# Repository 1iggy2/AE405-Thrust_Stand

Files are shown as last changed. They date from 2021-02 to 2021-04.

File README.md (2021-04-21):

# AE405 Thrust Stand

Aero 405 Thrust Stand Project

*By Cameron Gable (1iggy2), Anthony Russo, Hogan Hsu, Sergio Ramirez Sabogal, Brian Sandor*

This project is aimed towards providing a thrust testing stand for brushless electric motors
and propellers used by student project teams as part of Professor George Halow’s AERO 495
course. Prof. Halow has indicated that there is currently a need for some of the project teams that
are part of his course to have an easy way to test the thrust capabilities of their electric motors and
propellers for applications ranging from quadcopters to fixed wing aircraft. Our project concept is
therefore a proposal to design, build, and test a modular thrust test stand that allows for multiple
motor and propeller sizes to be tested safely and effectively by any of the teams participating in
AERO 495. This test stand will use sensors to measure thrust, torque, voltage, current, and RPM
and involve a processing system for automated data collection for simple export to software like
Excel or MatLab for analysis.

<p align="center">
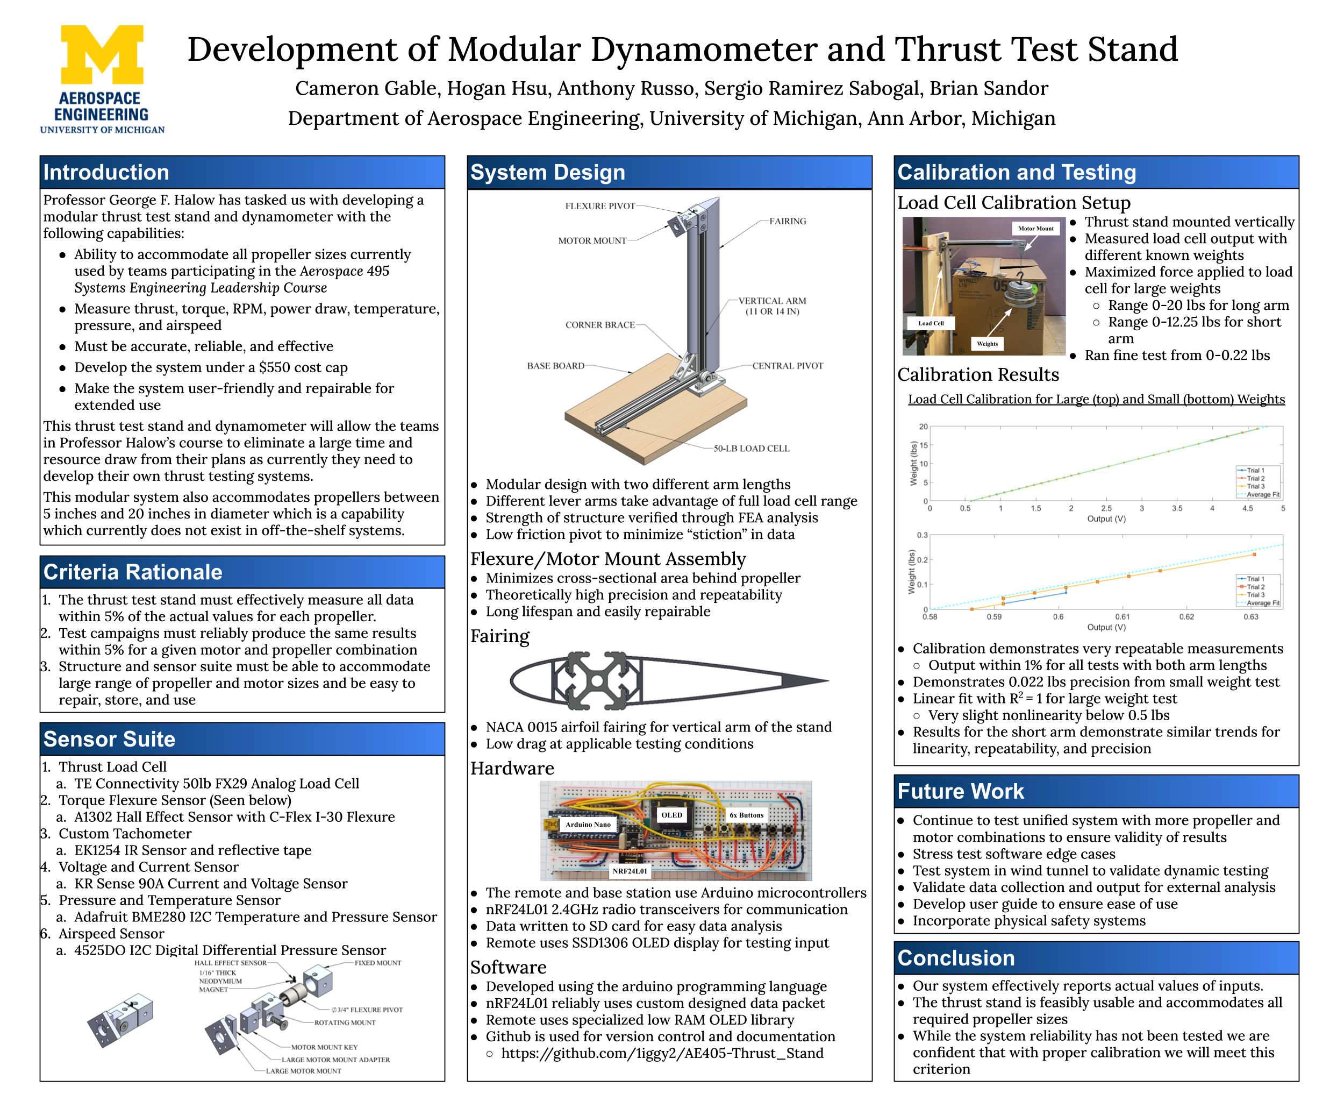
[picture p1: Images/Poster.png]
  
</p>

Table of Contents
=================

<!--ts-->
   * [Instruction Manual](#instruction-manual)
      * [Safety Considerations](#safety-considerations)
      * [How to Use the Remote](#how-to-use-the-remote)
      * [How to Use the Base Station](#how-to-use-the-base-station)
   * [Construction Guide](#construction-guide)
      * [Wiring](#wiring)
        * [Remote](#remote)
        * [Base Station](#base-station)
      * [Thrust Stand](#thrust-stand)
   * [Design Justification](#design-justification)
      * [Code](#code)
        * [Base Station Logic](base-station-logic)
        * [Remote GUI Explaination](remote-gui-explaination)
      * [Physical Structure Analysis and Testing](physical-structure-analysis-and-testing)
        * [Thrust Stand Simulation](thrust-stand-simulation)
<!--te-->

## Instruction Manual

### Safety Considerations

Be careful when near spinning and/or powered propellers they can and will maim you. Please remove all propellers while working on the thrust stand. Propellers of all sizes are dangerous and deserve your respect. Please use the remote to remain clear of the spinning blades of death, and ensure you have a way to break the physical circuit from a distance.

(http://www.youtube.com/watch?v=q4shbLB9U7Q "")

### How to Use the Remote

The remote connects to the base station using an nRF24L01 radio transciever. When powering on the remote from a computer or USB power supply you will be prompted to select a test to perform. The test selection buttons are on the left hand side of the remote and ordered as seen below:
* TS - Throttle Sweep
* CT - Constant Throttle
* ST - Stress Test
<p align="center">
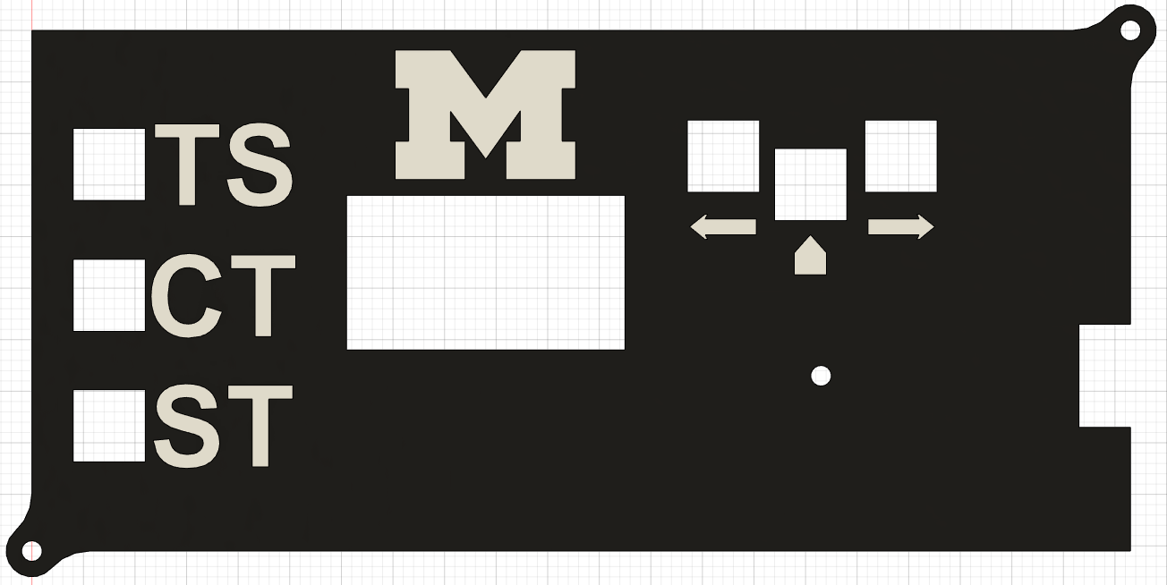
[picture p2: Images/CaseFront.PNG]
  
</p>
<p align="center">
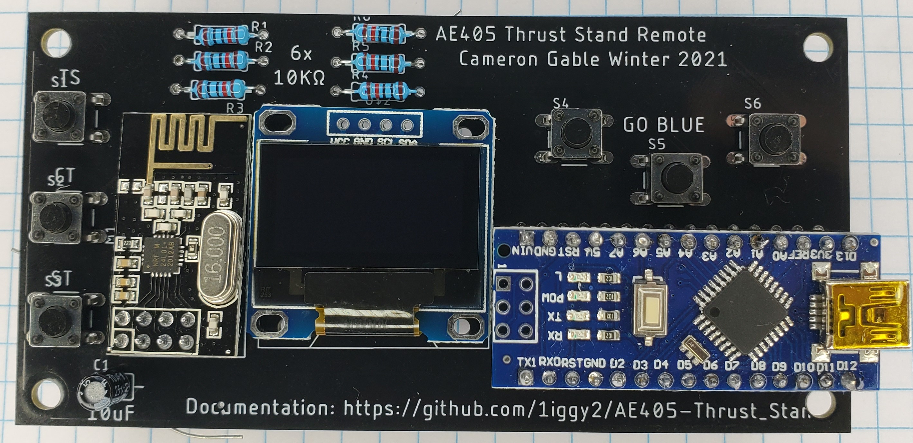
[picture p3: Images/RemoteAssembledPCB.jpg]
  
</p>
You then will use the ← (left), → (right), and ⌂ (select) buttons to enter your chosen testing parameters. These parameters are:
  
| Parameter |     Description    |  Throttle Sweep |    Constant Throttle    |     Stress Test     |
|:---------:|:------------------:|:---------------:|:-----------------------:|:-------------------:|
|     A     |      Test Type     |        1        |            2            |          3          |
|    BBB    |  Primary Throttle  | Bottom of Sweep | Constant Throttle Value | High Throttle Value |
|    CCC    | Secondary Throttle |   Top of Sweep  |           N/A           |  Low Throttle Value |
|    DDD    |      Test Time     | Total Test Time |     Total Test Time     |   Total Test Time   |
|    EEE    |      Step Time     |    Step Time    |           N/A           |    Switching Time   |

Before clicking to confirm your test selection and start your test you will be presented these values as a final check before sending the data to the base station. This will appear in the form:

* A:BBB:CCC:DDD:EEE

After the data is sent to the base station and the test begins simply click the ⌂ (select) button to send a cancel signal to the base station. In case of communication failure it is always important to have a safe method to physically break the circuit in the case of a catastrophic testing failure. 

### How to Use the Base Station

The base station is a rather hands off piece of equipment. You should not be interacting with it during testing, only monitoring. You may want to set your own safety parameters or recalibrate the test stand. In that case I recommend modifying the parameters in the base station file: [Mega_BaseStation.ino](https://github.com/1iggy2/AE405-Thrust_Stand/blob/main/Mega_BaseStation/Mega_BaseStation.ino) If you do this please submit your calibration to this Github page for posterity. To gather data you will need to insert a FAT32 or FAT16 formatted microSD card into the [Adafruit MicroSD card breakout board+](https://www.adafruit.com/product/254) for the data to be recorded. The data will be recorded to the microSD card in the format shown below. 

| AERO 405 Thrust Stand |                       Winter 2021                      |         |             | Cameron Gable |
|:---------------------:|:------------------------------------------------------:|:-------:|:-----------:|:-------------:|
| Find Documentation at:| [Github](https://github.com/1iggy2/AE405-Thrust_Stand) |         |             |               |
|                       |                                                        |         |             |               |
|  Ambient Conditions:  |                                                        |         |             |               |
|      Temperature:     |                          VALUE                         | Celsius |             |               |
|       Pressure:       |                          VALUE                         | Pascals |             |               |
|                       |                                                        |         |             |               |
|       Thrust(N)       |                          Volts                         |   Amps  | Torque(n-m) |      RPM      |
|         VALUE         |                          VALUE                         |  VALUE  |    VALUE    |     VALUE     |

At this time analysis software is not being developed. It is an important feature to this project, and the relevant issue can be found [here.](https://github.com/1iggy2/AE405-Thrust_Stand/issues/9)

## Construction Guide

### Wiring

#### Remote
The wiring diagram for the remote has been completed in EAGLE. Completed PCB design Gerber files can be found [here.](https://github.com/1iggy2/AE405-Thrust_Stand/tree/main/CAD/RemotePCB) The connections on the diagram below are accurate for anyone who prefers to manufacture it on perf board. (Assembling via a PCB is certainly easier though).

<p align="center">
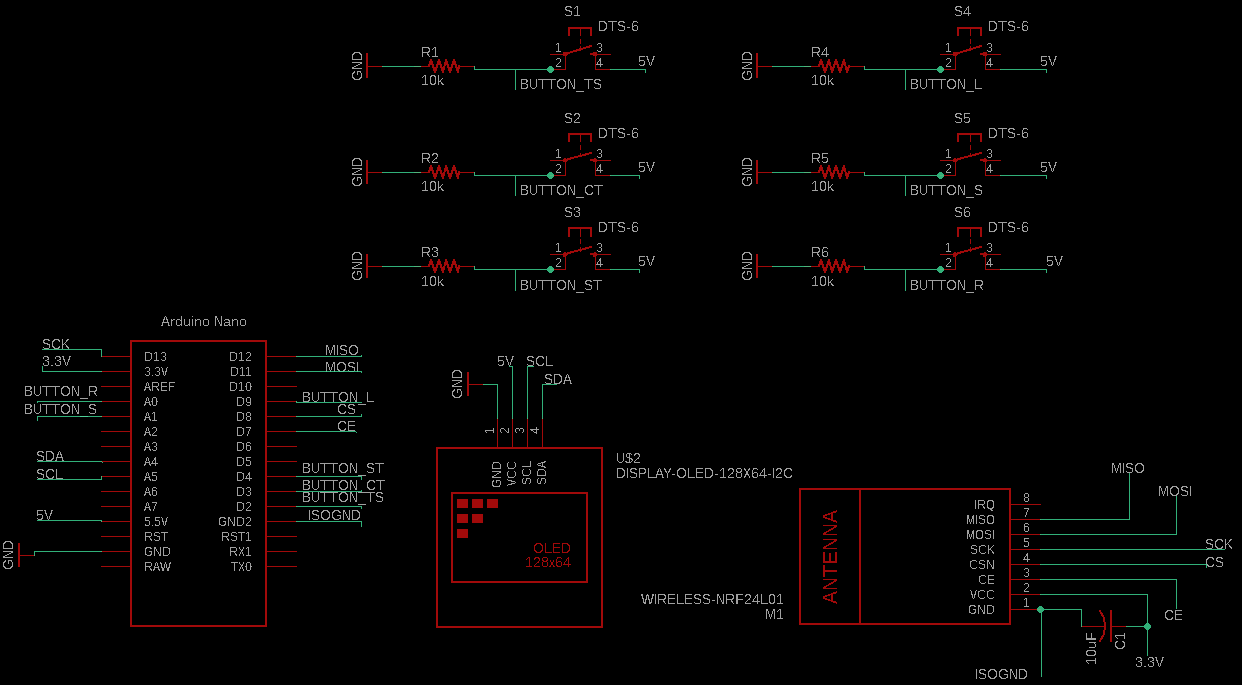
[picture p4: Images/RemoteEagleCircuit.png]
  
</p>

#### Base Station
The wiring diagram for the base station was also completed in EAGLE. However, a PCB has not yet been designed and remains an [issue](https://github.com/1iggy2/AE405-Thrust_Stand/issues/3) for future work.

<p align="center">
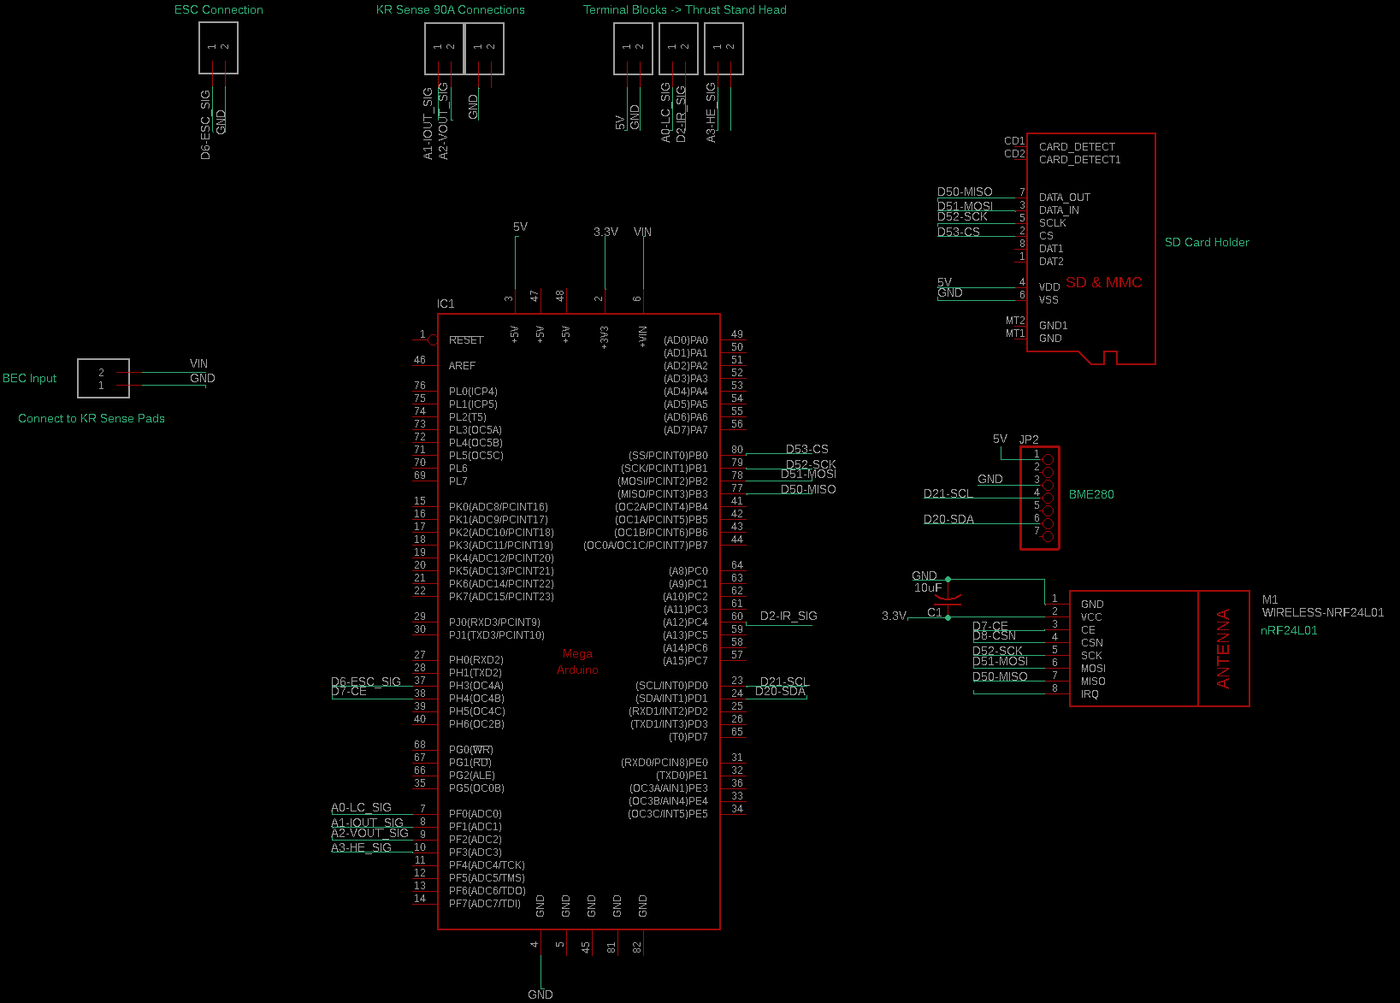
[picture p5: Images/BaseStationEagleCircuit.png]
  
</p>
Please note in the EAGLE image above the pin locations are not accurate on the Arduino Mega, instead the nets have been named [PIN-PURPOSE].

### Thrust Stand

Our thrust stand has been designed with modularity as the main objective. The interchangeable
vertical arm lengths allow for testing to occur for a variety of propeller and motor sizes. This also
allows for the thrust stand to operate in both large and small wind tunnels, making test scheduling more convenient for the users. Our motor mounting plates will allow for the mounting of
various motors with different bolt patterns. The various sizes of these plates will allow for testing
on small motors and large motors on the same stand. 

Long Arm Render             |  Short Arm Render
  :-------------------------:|:-------------------------:
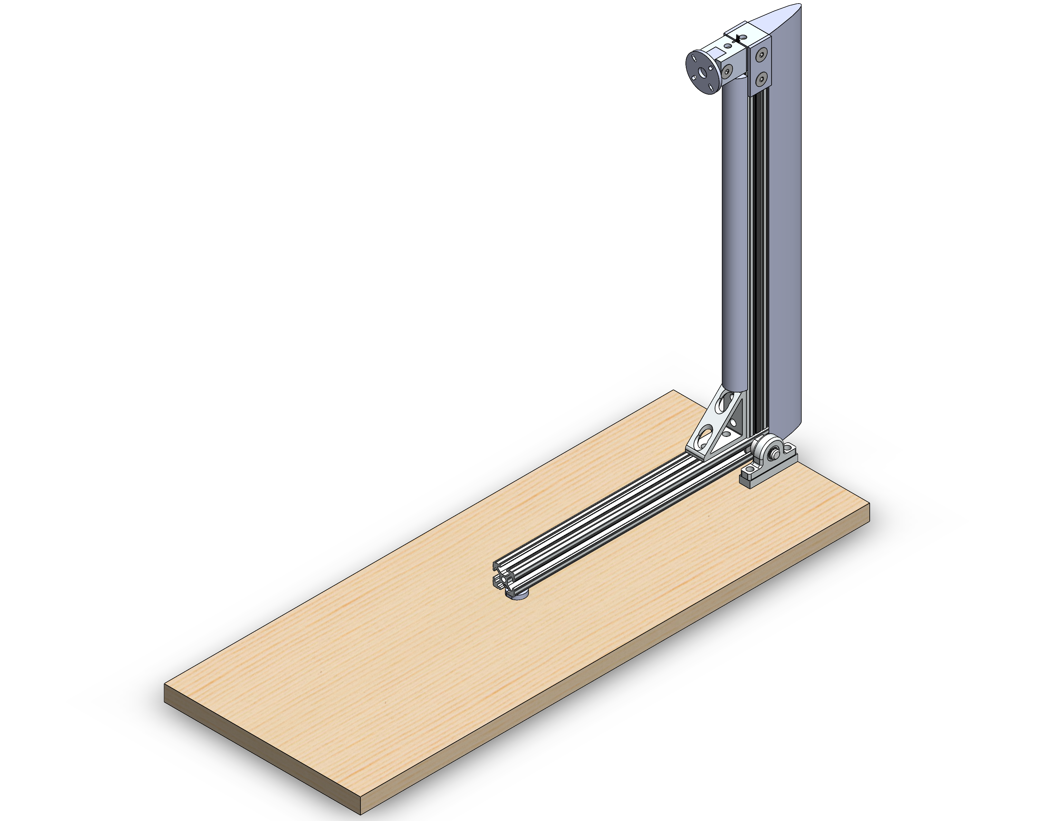
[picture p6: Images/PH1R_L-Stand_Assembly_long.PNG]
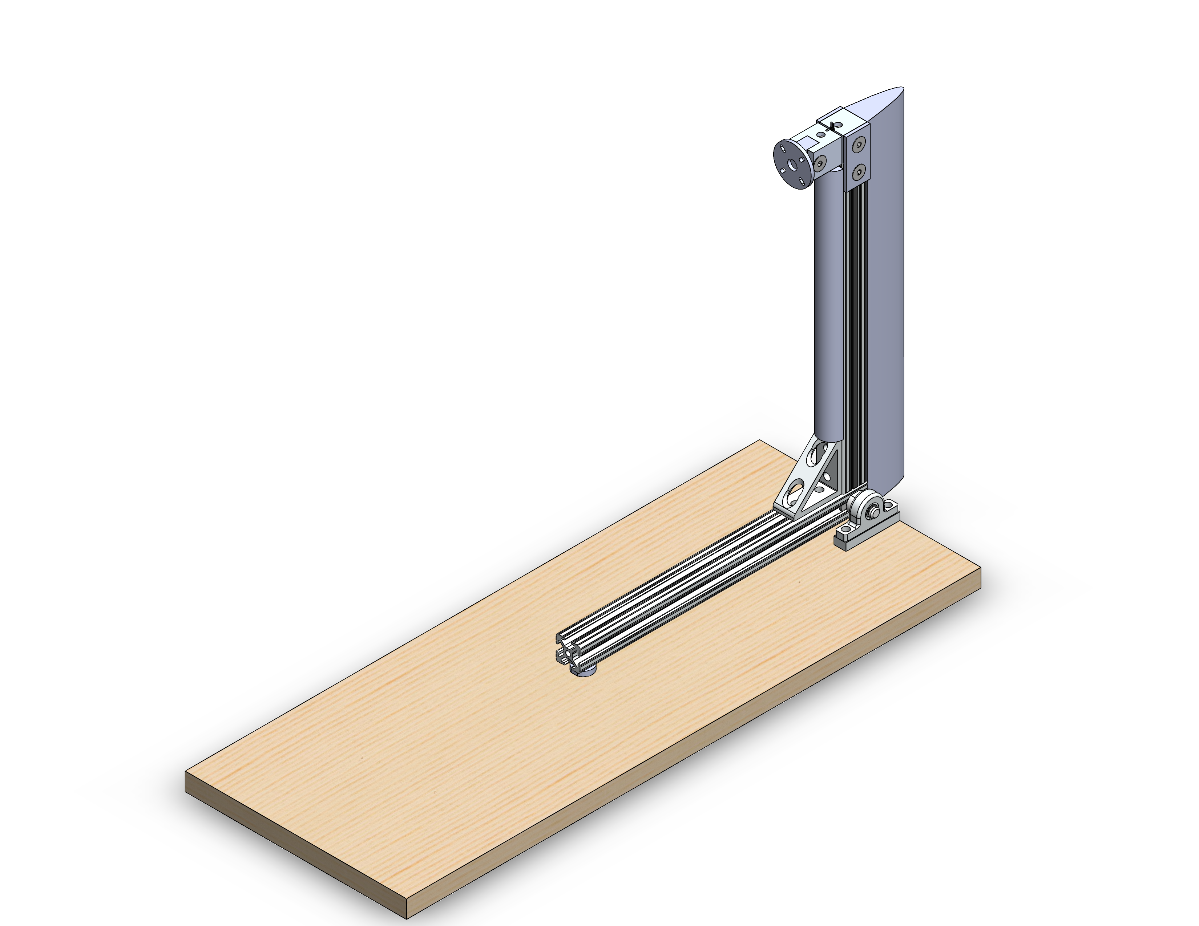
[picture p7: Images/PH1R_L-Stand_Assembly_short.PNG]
  |  

Our unique flexure torque measurement
device, seen below, allows for torque data to be collected from all ranges of motor sizes that fit on the thrust
testing stand. This innovation increases the effectiveness and accuracy of the data from other more
traditional torque measurement solutions. These system design choices increase the effectiveness
of our thrust stand and allow it to meet a wide variety of team’s thrust testing needs.
<p align="center">
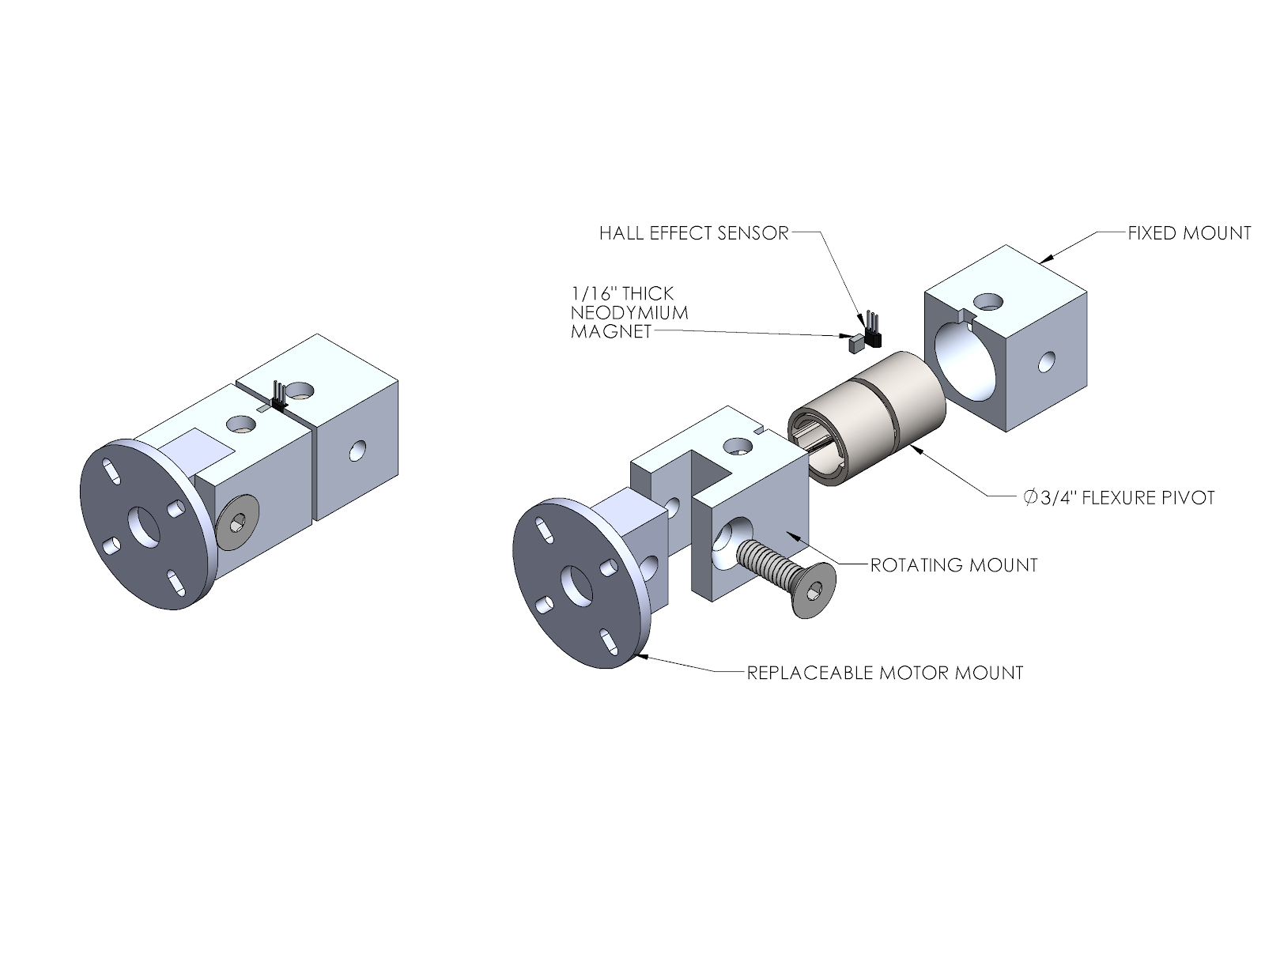
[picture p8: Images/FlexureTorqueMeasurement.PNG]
  
</p>
Our design also features a pivot comprised of two pillow blocks to minimize any stiction, or static friction. A beautiful render of this pivot is shown below. A majority of the parts purchased for the structural construction came from McMaster Carr.

<p align="center">
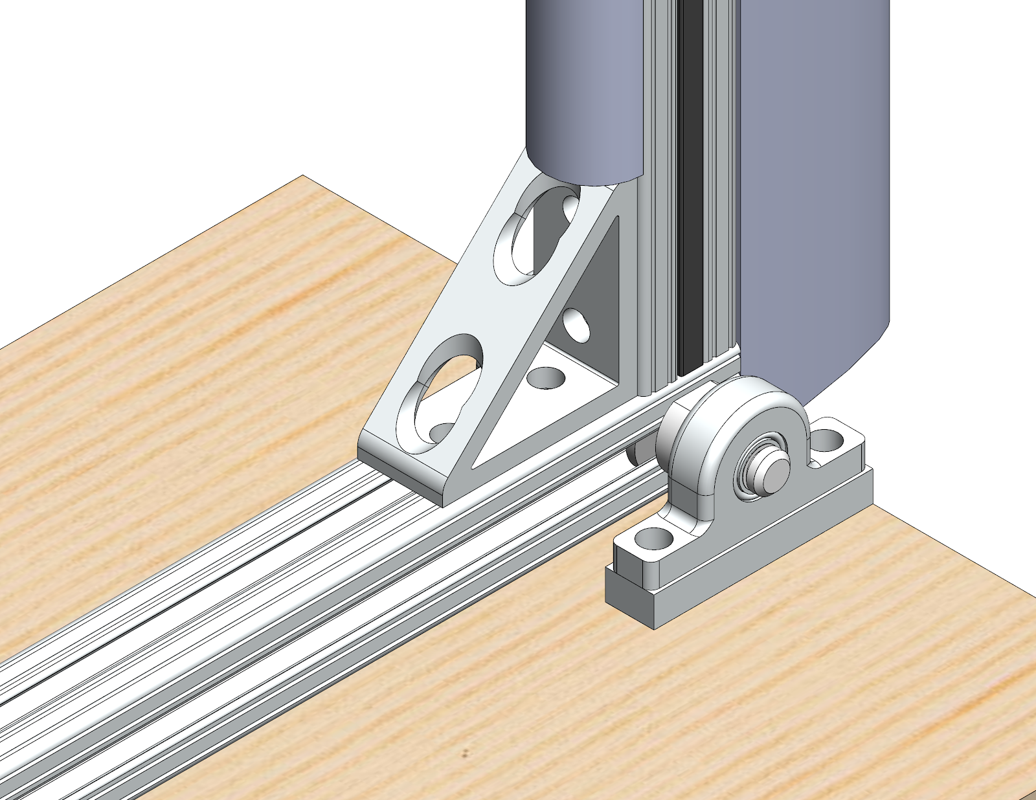
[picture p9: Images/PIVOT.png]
  
</p>

## Design Justification

### Code

#### Base Station Logic

The Base Station is the measurement and data acquistion hub of this project. Tests will be run based on the Menu ID sent from the remote. Raw sensor output, calibration, and settings will be accessed via a physical button press and the serial monitor. This is due to RAM limitations in the Arduino Nano powering the Remote. A full flowchart of the logic is provided below.

<p align="center">
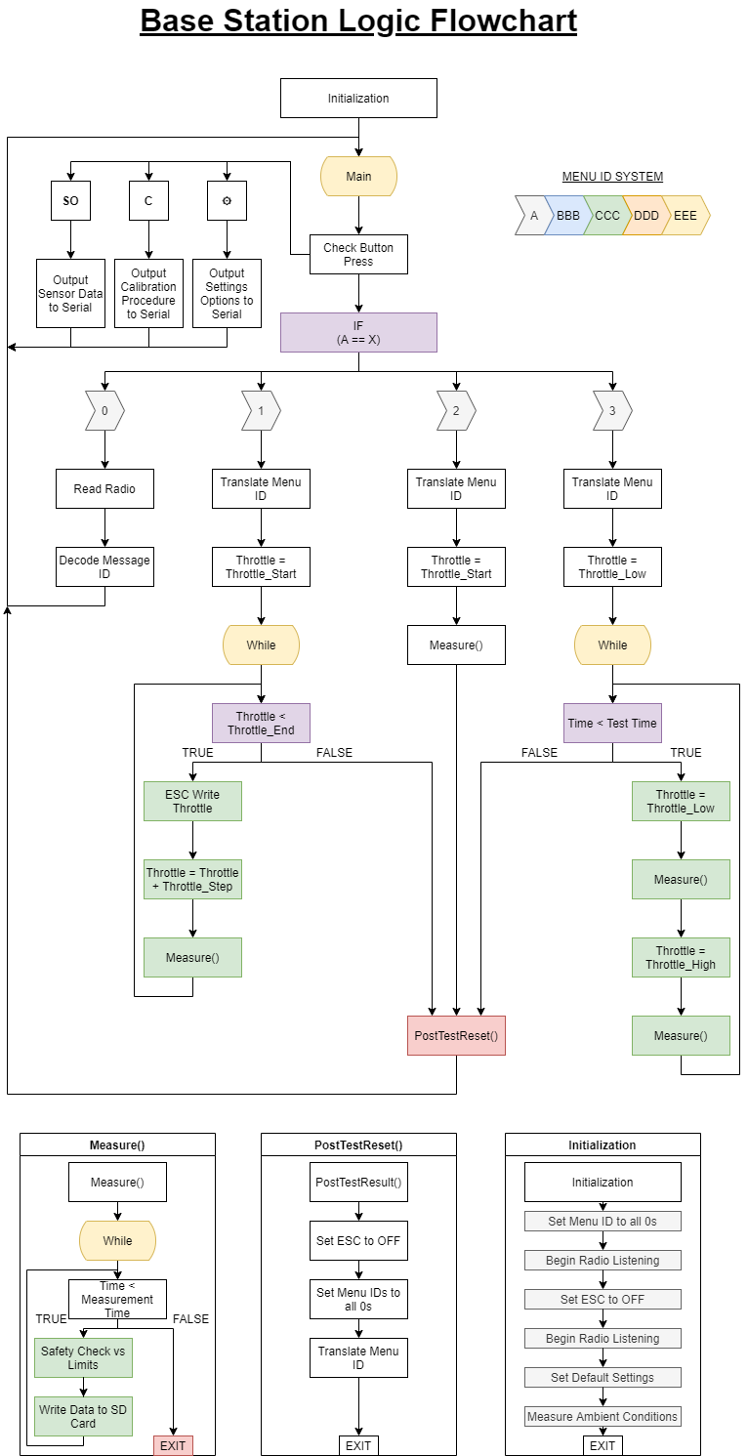
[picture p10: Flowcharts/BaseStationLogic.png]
  
</p>

#### Remote GUI Explaination

After initial testing of the remote GUI intiailly proposed it was apparent that the Arduino Nano did not have enough RAM to display the fully fleshed out GUI. In order to combat this we have designed a low menu count GUI to optimize the remote. This menu uses a minimal amount of unique screens to lower the RAM usage. The image below is the design flowchart for the optimized remote.

<p align="center">
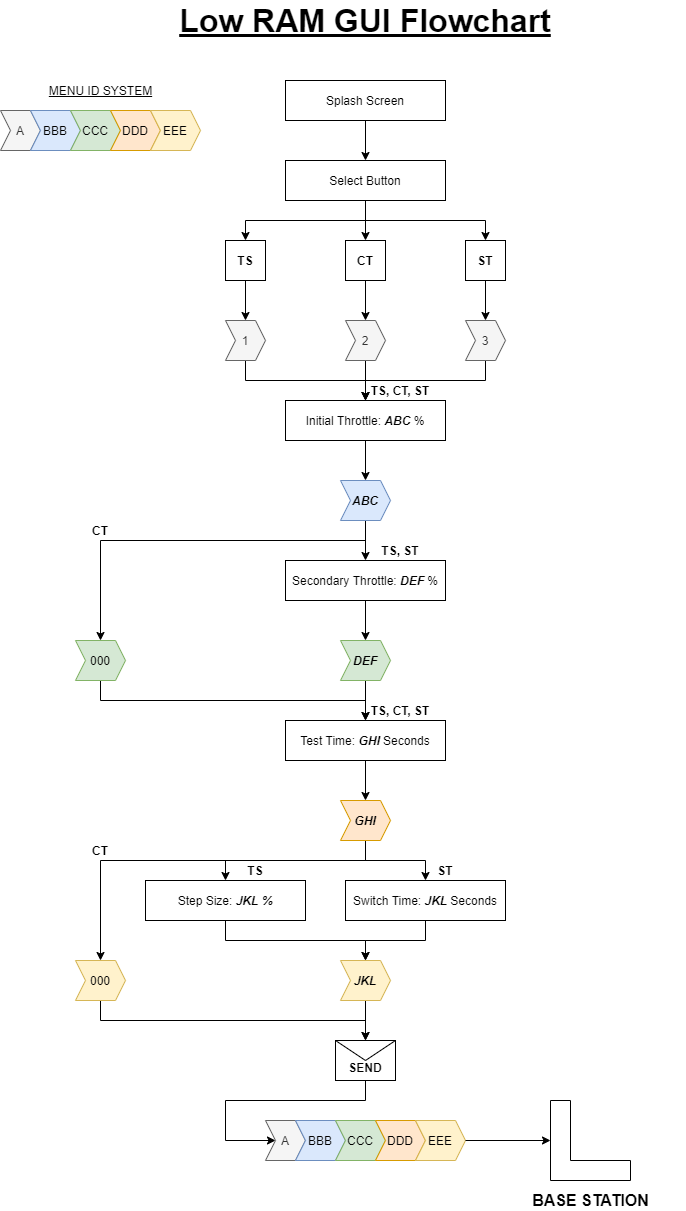
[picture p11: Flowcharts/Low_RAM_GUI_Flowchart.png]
  
</p>

### Physical Structure Analysis

#### Thrust Stand Simulation

In order to model the thrust stand system in FEA many of the complex structures
were simplified. This included the flexure assembly being modelled as a rectangular block and
the bearing pivot being modelled as a bearing fixture. The CAD model was done in Solidworks
and the FEA was done in the Solidworks built-in simulation tool. The load cell and the sides of the
pivot were modelled as roller/slider fixtures so that they would be constrained in the plane but
can move laterally. The built-in 6061 aluminum alloy material model was applied to the model
due to convenience, which has the same properties as the 6105-T5 alloy, just a lower yield strength.
The mesh was generated using Solidworks’ automated mesh tool, but mesh control was applied
in order to ensure that there were at least 3 elements across each dimension to accurately model
the problem. In the image below, a zoomed in display of the maximum stress point is shown along with
the mesh for the max loading condition of 20 lbf of thrust and 15 lbf-in of torque on the long
arm model. The maximum stress ended up being in the same region for all the simulations, right
where the 90◦ bracket met the horizontal arm.

<p align="center">
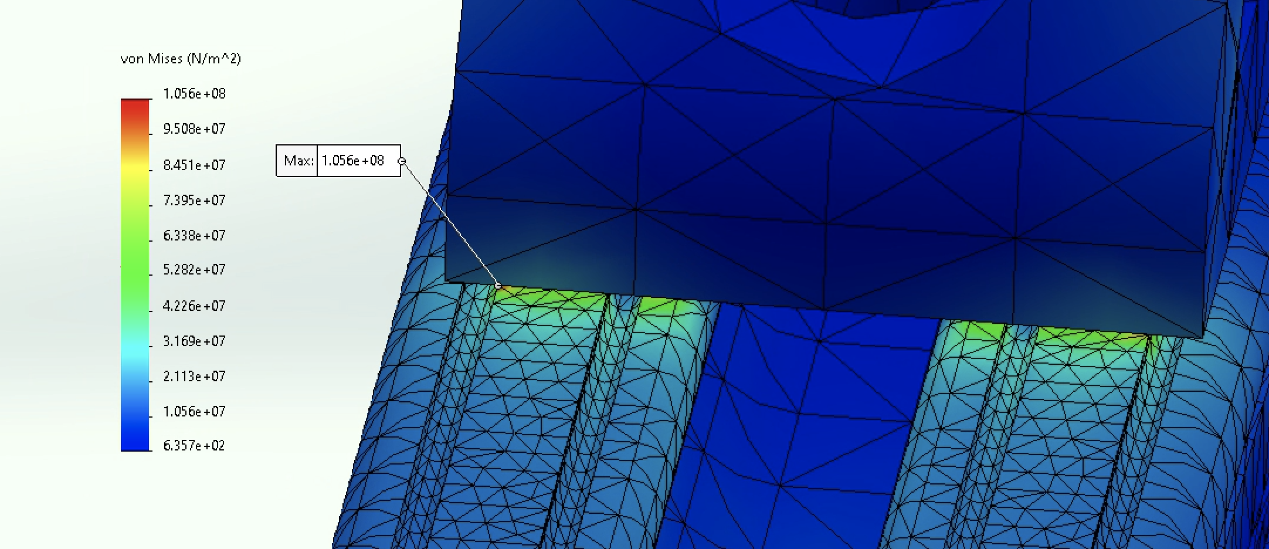
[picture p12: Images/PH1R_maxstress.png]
  
</p>

Another accuracy concern is the drag produced by inlet air during wind tunnel testing, particularly
on the vertical arm of the test stand. The load cell measuring thrust will not be able to distinguish between this drag force and a thrust difference, thus reducing accuracy. To make sure that
our measurement is as accurate as possible during these testing circumstances, we surveyed various cross-sectional shapes of the vertical beam using CFD simulations. STAR-CCM+ CFD simulations were used to model the drag of the
stand. Because the only variable between these design is the vertical beam cross-section, simulations were performed using the 15 inch beam by itself, with semicircular fairings, and with one
semicircular fairing on the front face and an elliptical section on the rear face to give the overall cross-section an airfoil shape. Seen in the table below.

| No Fairing | Semi-Circular Fairing | Airfoil Fairing |
|------------|-----------------------|-----------------|
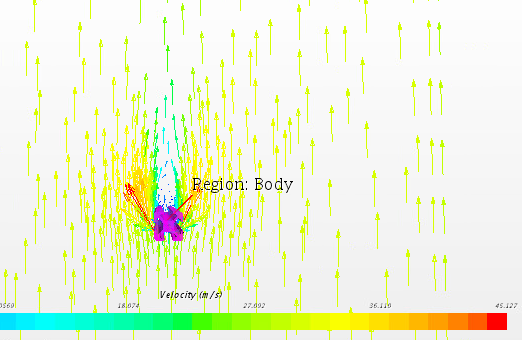
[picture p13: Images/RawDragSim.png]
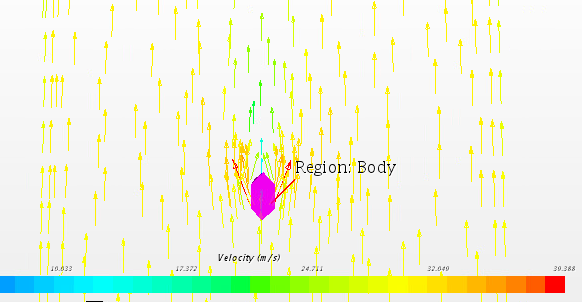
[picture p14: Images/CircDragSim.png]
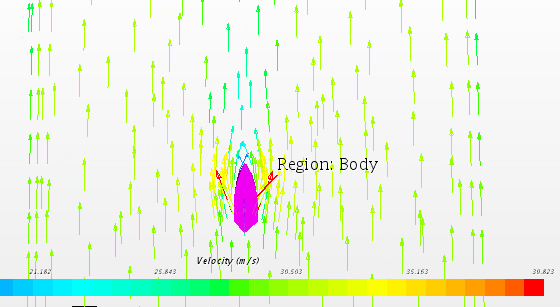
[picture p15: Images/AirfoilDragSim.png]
|       |                  |            |

The simulations were then run with the respective beam suspended,
centered in a simulated 2 foot X 2 foot wind tunnel using iterations with intake airspeed of 11, 22,
34, 45, 56, and 67 miles per hour. The results are shown in the table below.

<p align="center">
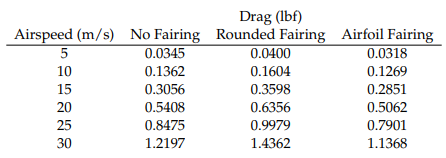
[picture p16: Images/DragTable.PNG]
  
</p>

Plotted into a graph:

<p align="center">
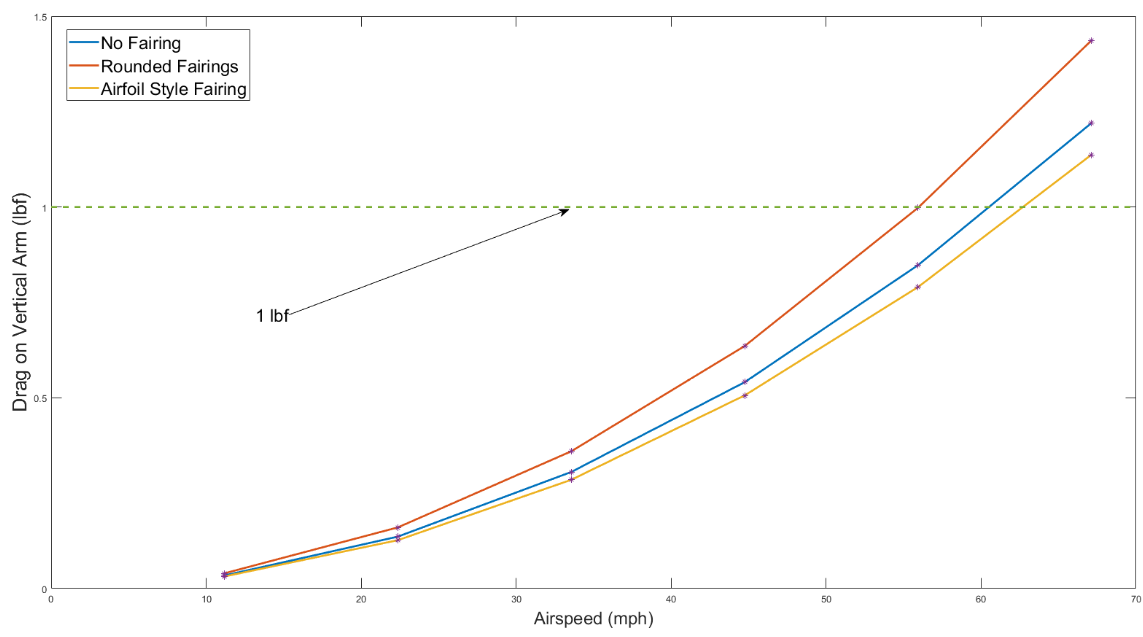
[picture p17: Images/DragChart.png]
  
</p>

With this information we are designing a 3D printed airfoil to slot into the 8020 aluminium extrusion. We will also be putting our structure, shrouded with an aerodynamic
fairing, into the wind tunnel and testing the amount of drag that the system generates with the
goal of minimizing this effect. This will be to validate our simulations. 

We chose to use a NACA 0015 airfoil fairing for the vertical arm of the stand.

<p align="center">
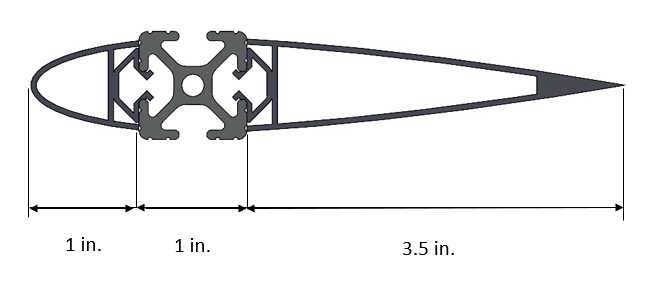
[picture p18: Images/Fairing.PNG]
  
</p>

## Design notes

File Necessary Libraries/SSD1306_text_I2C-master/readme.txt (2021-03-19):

SSD1306_text -- methods
April 2015

init() - call once in setup
clear() - clears screen, sets cursor to 0,0
setCursor(row, pixel_col) - sets cursor to row (0..7) and pixel_column (0..127)
setCursor(row) - sets cursor to row (0..7) and pixel_column=0 
getRow() - returns current row
getCol() - returns current column
setTextSize(size, spacing) - sets text size (1..8) and pixel spacing between chars (0,1,2,...)
setTextSize(size) - sets text size (1..8) and sets spacing to the same value
write(c) - write a single character to the current cursor location with current size/spacing
write(*str) - write a string of characters
write(*buffer, nBytes) - write nBytes of characters from a buffer
sendData(b) - write an 8-bit vertical slice of pixels to the current cursor location

Configuration switches in the .h file provide for choosing hardware SPI, software SPI or I2C
support. Also support for scaled fonts larger than the default 5x7 (size=1) can be enabled/disabled. In addition, improved fonts for the numeric characters 0-9 for sizes 2x, 3x and 8x the 5x7 font size can be enabled/disabled.

With a minimum configuration (H/W SPI and no scaled or larger fonts) a simple "hello world" sketch is about 2500 bytes in size and uses about 50 bytes of RAM. Adding scaled fonts increases the code size somewhat. Adding dedicated larger numeric fonts has a more pronounced effect on code size.

I2C support uses the Wire library which, in addition to adding ~1K of code, adds about 200 bytes of RAM usage, mostly from the five 32-byte buffers in the library.

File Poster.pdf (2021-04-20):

System Design

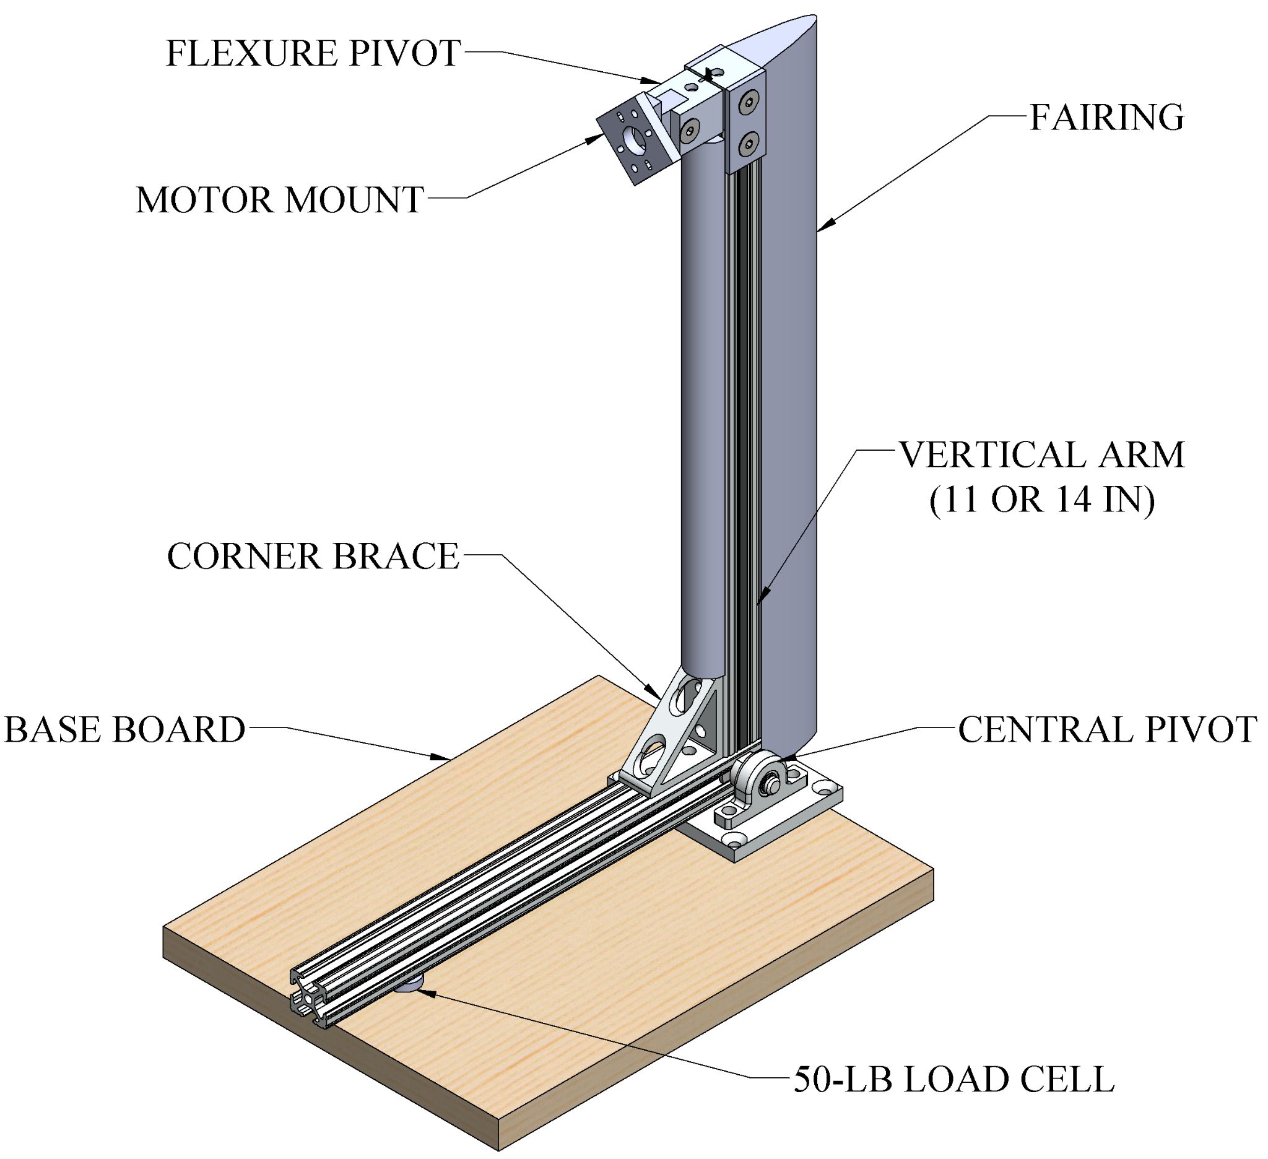
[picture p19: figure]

- Modular design with two different arm lengths
- Different lever arms take advantage of full load cell range
- Strength of structure verified through FEA analysis
- Low friction pivot to minimize “stiction” in data

## Flexure/Motor Mount Assembly

- Minimizes cross-sectional area behind propeller
- Theoretically high precision and repeatability
- Long lifespan and easily repairable

## Fairing

- NACA 0015 airfoil fairing for vertical arm of the stand
- Low drag at applicable testing conditions

## Hardware

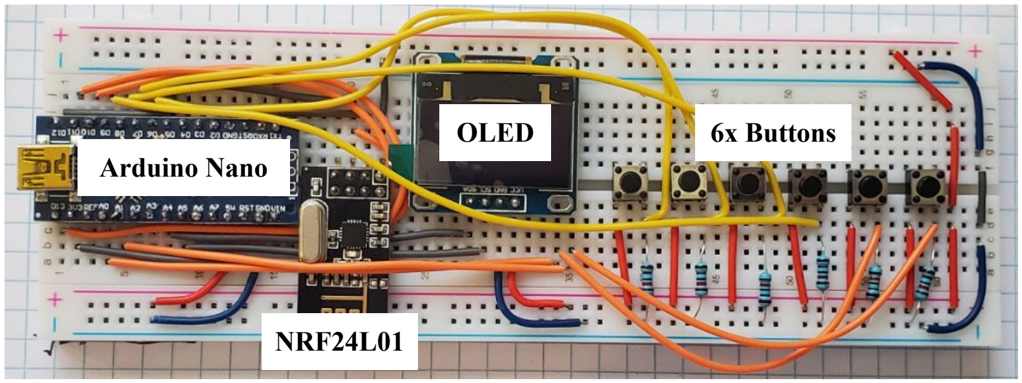
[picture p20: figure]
Arduino Nano; OLED; NRF24L01; 6x Buttons

- The remote and base station use Arduino microcontrollers
- nRF24L01 2.4GHz radio transceivers for communication
- Data written to SD card for easy data analysis
- Remote uses SSD1306 OLED display for testing input

## Software

- Developed using the arduino programming language
- nRF24L01 reliably uses custom designed data packet
- Remote uses specialized low RAM OLED library
- Github is used for version control and documentation
- https://github.com/1iggy2/AE405-Thrust_Stand

# Development of Modular Dynamometer and Thrust Test Stand

## Cameron Gable, Hogan Hsu, Anthony Russo, Sergio Ramirez Sabogal, Brian Sandor Department of Aerospace Engineering, University of Michigan, Ann Arbor, Michigan

Introduction
Professor George F. Halow has tasked us with developing a modular thrust test stand and dynamometer with the following capabilities:
- Ability to accommodate all propeller sizes currently used by teams participating in the Aerospace 495 Systems Engineering Leadership Course
- Measure thrust, torque, RPM, power draw, temperature, pressure, and airspeed
- Must be accurate, reliable, and effective
- Develop the system under a $550 cost cap
- Make the system user-friendly and repairable for extended use
This thrust test stand and dynamometer will allow the teams in Professor Halow’s course to eliminate a large time and resource draw from their plans as currently they need to develop their own thrust testing systems.
This modular system also accommodates propellers between 5 inches and 20 inches in diameter which is a capability which currently does not exist in off-the-shelf systems.

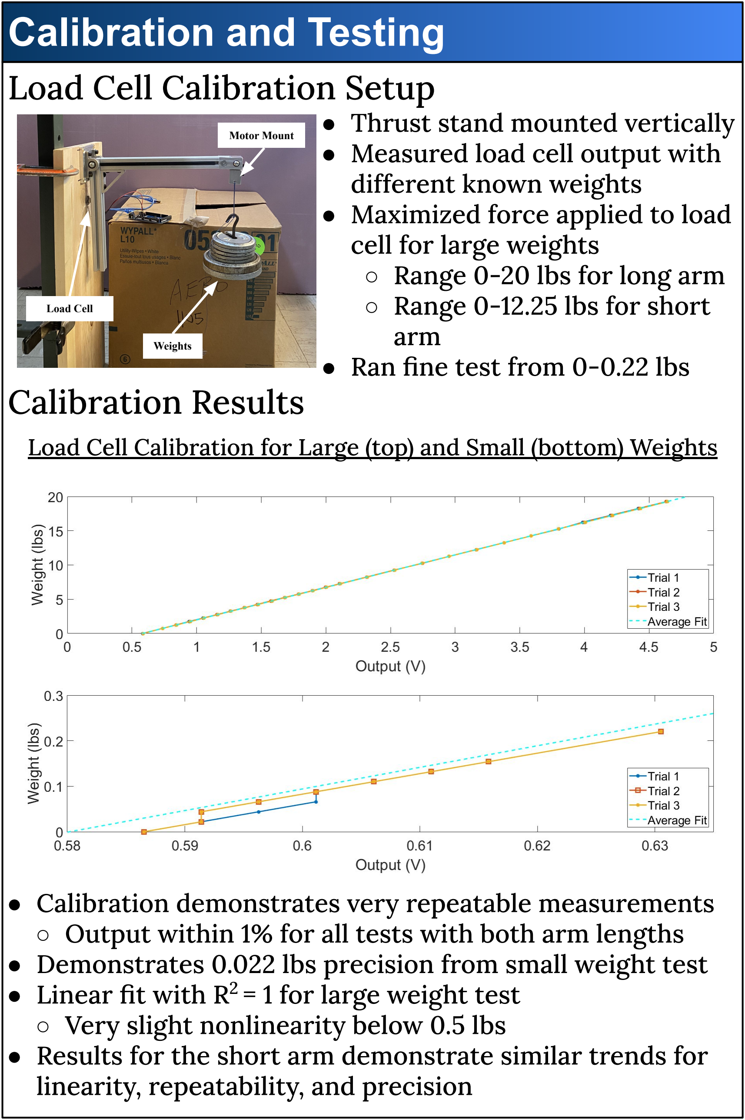
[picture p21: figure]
Calibration and Testing Load Cell Calibration Setup ● Thrust stand mounted vertically ● Measured load cell output with different known weights ● Maximized force applied to load cell for large weights ○ Range 0-20 lbs for long arm ○ Range 0-12.25 lbs for short arm ● Ran fine test from 0-0.22 lbs; Calibration Results; ● Linear fit with R; 2 = 1 for large weight test; linearity, repeatability, and precision; Weights; Load Cell; Motor Mount

Load Cell Calibration for Large (top) and Small (bottom) Weights

- Calibration demonstrates very repeatable measurements
- Output within 1% for all tests with both arm lengths
- Demonstrates 0.022 lbs precision from small weight test
- Very slight nonlinearity below 0.5 lbs
- Results for the short arm demonstrate similar trends for

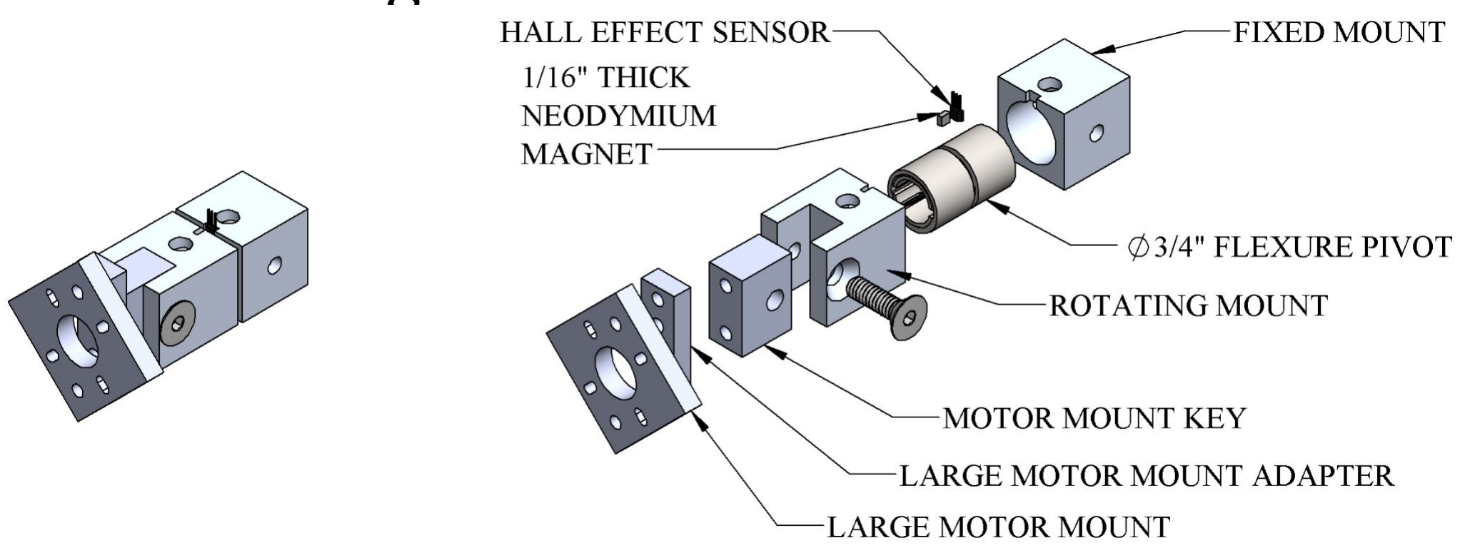
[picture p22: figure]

Conclusion
- Our system effectively reports actual values of inputs.
- The thrust stand is feasibly usable and accommodates all required propeller sizes
- While the system reliability has not been tested we are confident that with proper calibration we will meet this criterion

Criteria Rationale
1. The thrust test stand must effectively measure all data within 5% of the actual values for each propeller.
2. Test campaigns must reliably produce the same results within 5% for a given motor and propeller combination
3. Structure and sensor suite must be able to accommodate large range of propeller and motor sizes and be easy to repair, store, and use

Sensor Suite
1. Thrust Load Cell
a. TE Connectivity 50lb FX29 Analog Load Cell
2. Torque Flexure Sensor (Seen below)
a. A1302 Hall Effect Sensor with C-Flex I-30 Flexure
3. Custom Tachometer
a. EK1254 IR Sensor and reflective tape
4. Voltage and Current Sensor
a. KR Sense 90A Current and Voltage Sensor
5. Pressure and Temperature Sensor
a. Adafruit BME280 I2C Temperature and Pressure Sensor
6. Airspeed Sensor
a. 4525DO I2C Digital Differential Pressure Sensor

Future Work
- Continue to test unified system with more propeller and motor combinations to ensure validity of results
- Stress test software edge cases
- Test system in wind tunnel to validate dynamic testing
- Validate data collection and output for external analysis
- Develop user guide to ensure ease of use
- Incorporate physical safety systems

# References

“NACA 0015,” Airfoil Tools. 2021 http://airfoiltools.com/airfoil/details?airfoil=naca0015-il

## “Brushless Motor and Propeller Thrust Stands,” RCbenchmark Available:https://www.rcbenchmark.com/

## Hossain M. R., Krouglicof, N.,"Propeller Dynamometer for Small Unmanned Aerial Vehicle,"CCECE2010, 2010.https://ieeexplore.ieee.org/document/5575152

## Asson, K. M., Dunn, P. F., "Compact Dynamometer System that Can Accurately Determine

PropellerPerformance,"Journal of Aircraft, vol. 29, pp. 8-9,

## 1992.https://arc-aiaa-org.proxy.lib.umich.edu/doi/abs/10.2514/3.46118

## Li, H. H., Davis, K. R., Davy, M. H. Green, S. I. "A Marine Propeller Aerodynamic Test

Facility,"Strain, vol. 43, pp. 125-131,

## 2007.https://doi-org.proxy.lib.umich.edu/10.1111/j.1475-1305.2007.00325.x

## "AA Standards Grade 6105 T5." Matmatch Available:https://matmatch.com/materials/alky16105229t50-aa-standards-grade-6105-t517

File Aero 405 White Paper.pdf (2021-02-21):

## White Paper: Modular Thrust Stand

Anthony Russo, Brian Sandor, Cameron Gable, Hogan Hsu, Sergio Ramirez Sabogal
February 3rd
, 2021

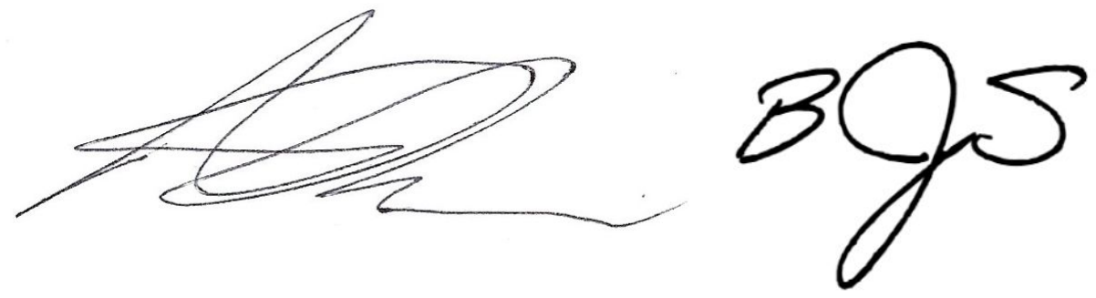
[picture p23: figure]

Description
This project identifies a direct need from the Aerospace 495 System Engineering Leadership Course (Aero 495) for testing hardware specifically for electric propeller-driven aircraft. The course focuses on leveraging three existing Student Project Teams: Michigan Vertical Flight Technology (MVFT), Michigan Drone Racing (MDR), and MACH (University of Michigan AIAA Design, Build, Fly Team). These three teams all rely on electric motors and propellers to propel their vehicles for competition. Each team uses different motor and propeller combinations ranging from roughly 5 inch propellers (MDR) to propellers larger than 15 inches (MVFT) and all teams need to perform in-house thrust testing to ensure consistent and reliable performance of their motors. As such, this team has been formed to develop a thrust testing system that can adequately meet the needs of the teams in Aero 495 as well as any future teams that may participate in the course or any other student project teams that use electric motors and propellers as their main propulsion system.
Our thrust testing system must be able to accommodate a range of propeller sizes and record thrust, revolutions per minute (RPM), motor torque, and power draw, as well as any other data that the aforementioned teams may want to analyze during their testing. Our system will also be safe, reliable, easy to repair and operate, meet the course cost cap, and use any and all available resources. We will be developing this testing system to be utilized by the aforementioned course and project groups. The goal being to create and test a more quality product than what is available off-the-shelf with much more operational flexibility and much higher quality results. This will be developed over the course of the Winter 2021 semester at the University of Michigan Aerospace Engineering facilities with the oversight and support of Professors George Halow (Aero 495) and Tim Smith (Aero 405).

Justification
The creation of the Aero 495 System Engineering Leadership Course this year has brought together many aerospace focused student project teams. These project teams share a need for thrust data from various electric motors. This has inspired our proposal of a modular thrust testing stand. This project will allow for streamlined thrust testing across all teams involved in the course. Individual solutions to this common problem cost students valuable time and money. In the spirit of collaboration, our unified modular solution will allow for rapid testing and data analysis for all teams involved. Our sponsor, Professor Halow, has enthusiastically endorsed this project for the value it brings to the project teams.

Impact/Effect
We estimate that our project will affect roughly 100 people per semester since it mostly benefits student project teams that work with propeller-based propulsion systems, in addition to the 495 lab. The main benefit of our project will be that it will allow for easier thrust testing of propellers for project teams within the Aerospace Engineering Department. This removes the need for teams to purchase or build their own thrust stands which may vary in reliability, safety and accuracy. Our aim is to improve upon existing thrust stands available for purchase like the RCbenchmark 1585 series thrust stand [1] which only allows for testing up to 5 kgf of thrust and a limited range of propeller diameters. We want to be able to test a range of propellers approximately between 5 and 20 inches in diameter which can easily go well above 5 kgf of thrust. As a result, we will be designing our thrust stand to be as modular as possible to allow for a wide range of motor sizes with minimal modification to the design as a whole. In addition to thrust, we want to be able to measure additional metrics such as voltage, current, torque, and RPM so we can also analyze the power and efficiency of the propulsion system being tested. Our thrust stand will be capable of recording all of this data autonomously and also perform some basic analysis to determine some dimensionless performance coefficients. To improve dynamic thrust testing accuracy, we will also attempt to minimize the cross section of this design to minimize flow-blockage. Finally, we will add electrical, physical, and procedural safety features into our design so the thrust stand can be used in the future without incident.

Sponsor
The main sponsor for this project is Professor George Halow specifically to benefit the Aero 495 System Engineering Leadership Course. The established communications plan is to combine our scheduled team briefings with Professor Tim Smith as part of the Aero 405 course with our briefings with Professor Halow. These meetings will maintain a bi-weekly schedule via Zoom and provide both interested parties the necessary information to remain up-to-date with our progress and ensure our system continues to meet the requirements of our sponsor as well as the Aero 405 course. Internally, team communication will be an obstacle, given the restrictions due to COVID-19. Our team has a designated channel on Discord to discuss project related matters at any time. We also plan to meet weekly via a Discord voice channel.

Evaluation of Resources
Thrust stands able to measure thrust, RPM, motor torque, and power draw have been previously built and can be bought off the shelf [1]. However, existing off-the-shelf thrust stands are normally lower quality in construction and cost significantly more than building a custom stand. There have been custom built thrust stands for various projects, but they are normally built for their individual projects in the case of Duvall and Theys [2,4]. These stands serve their purpose very well, but since they are designed for such a small use-case, they do not offer very much modularity for different sized propulsion systems. There have also been other innovative small propeller thrust stands, including utilizing strain gauges to determine thrust from beam bending, but this solution was unable to gather any torque or RPM data [3]. We believe we can fill an existing need by developing a modular thrust stand that is higher quality than those found off the shelf and that can be general use and accommodate a wide range of propeller sizes.

References
[1] “Brushless Motor and Propeller Thrust Stands,” RCbenchmark Available: https://www.rcbenchmark.com/.
[2] Duvall, Brian E.. “Development and Implementation of a Propeller Test Capability for Gl-10 “Greased Lightning” Propeller Design,” Master of Science (MS), thesis, Aerospace Engineering, Old Dominion University
[3] Marchman, C. S., “Thrust sensing for small UAVs,” Masters Theses, Missouri University of Science and Technology, (https://www.mst.edu/) 2016
[4] Theys, B., Dimitriadis, G., Hendrick, P., and Schutter, J. D., “Influence of propeller configuration on propulsion system efficiency of multi-rotor Unmanned Aerial Vehicles,” 2016 International Conference on Unmanned Aircraft Systems (ICUAS), Jun. 2016.

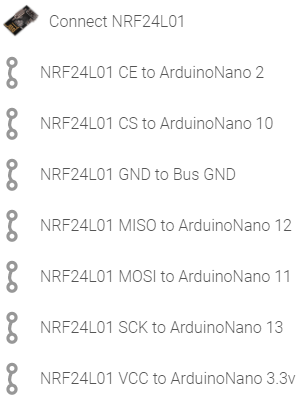
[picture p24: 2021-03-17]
Images/nRF24L01 Connections.PNG

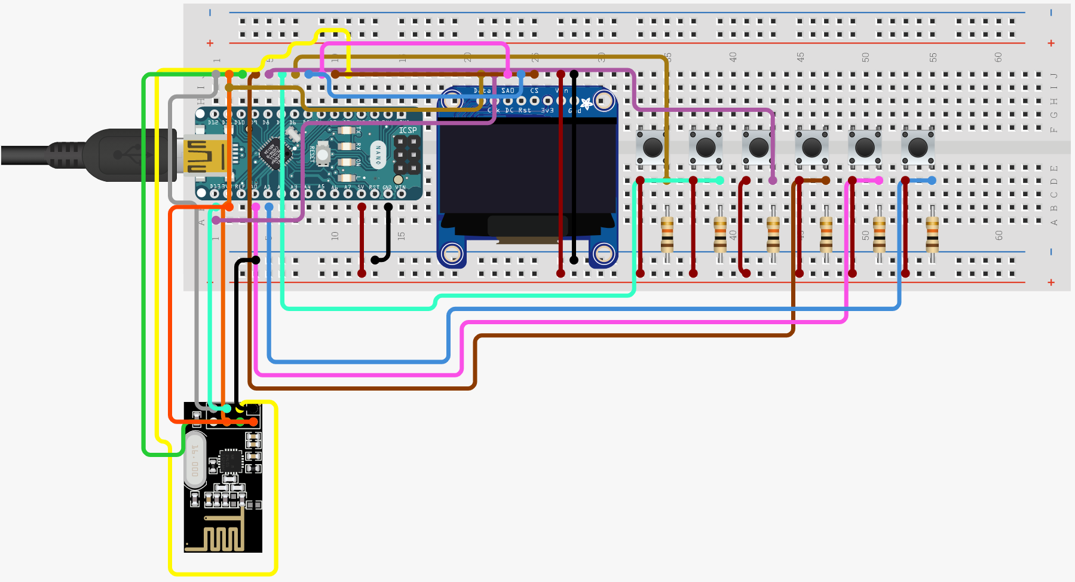
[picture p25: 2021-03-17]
Images/RemoteCircuitoDiagram.PNG

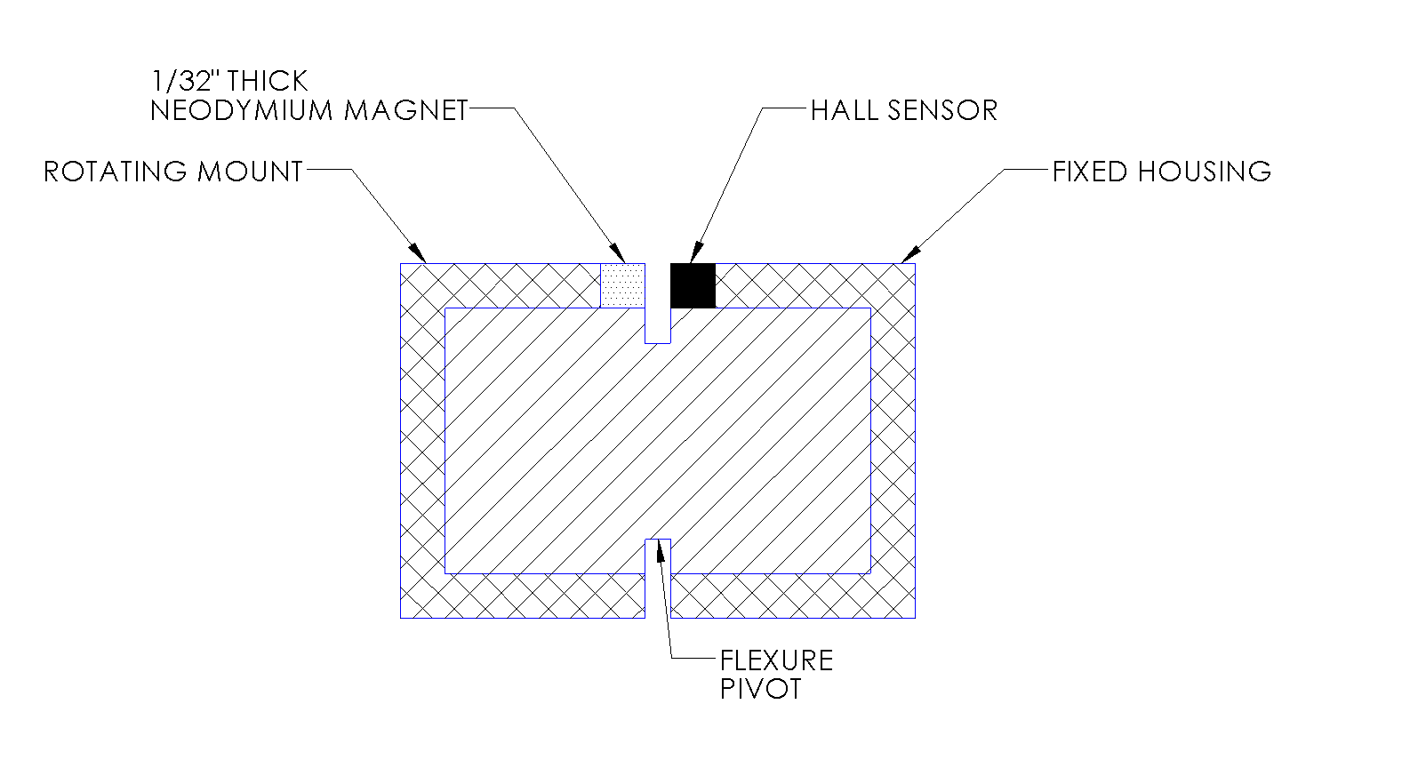
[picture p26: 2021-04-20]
Images/FlexurePivot.PNG

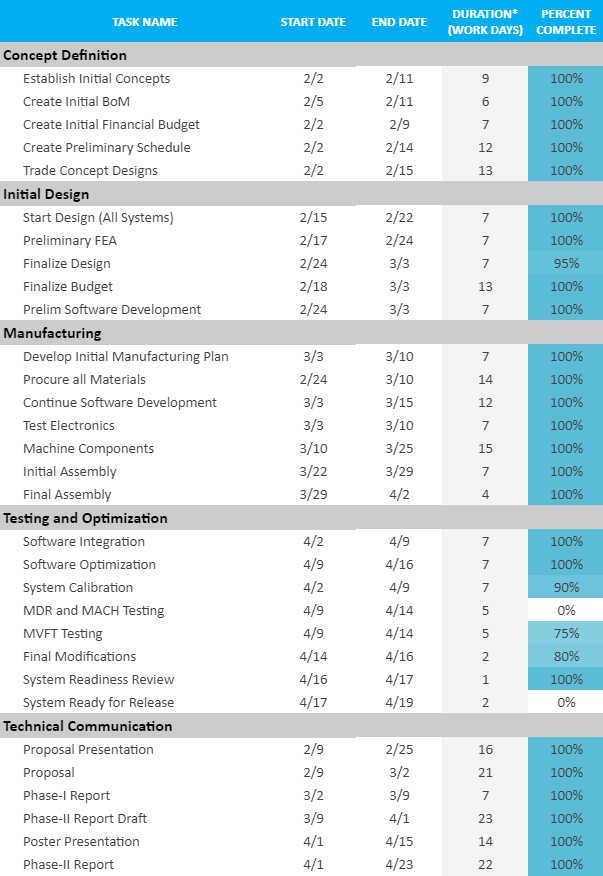
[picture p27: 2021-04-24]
Images/FinalScheduleDetails.PNG

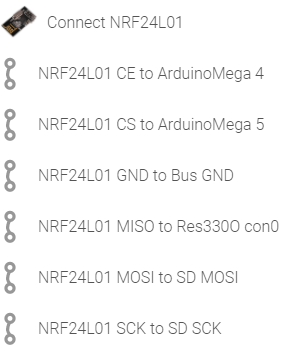
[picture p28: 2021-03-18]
Images/nRF24L01 Connections_MEGA.PNG

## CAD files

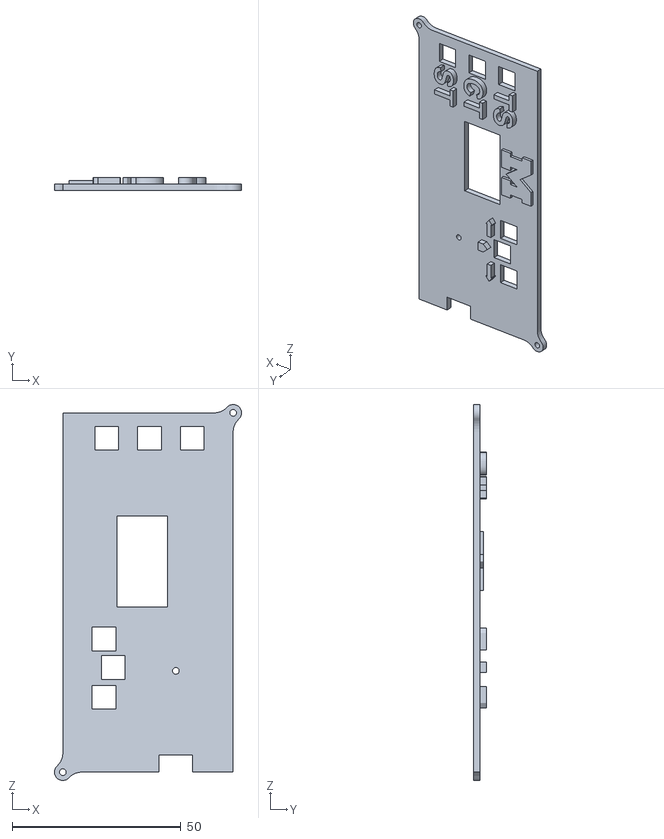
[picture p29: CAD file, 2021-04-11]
CAD/Remote/Lid.stl
55.5 x 4.00 x 111.5

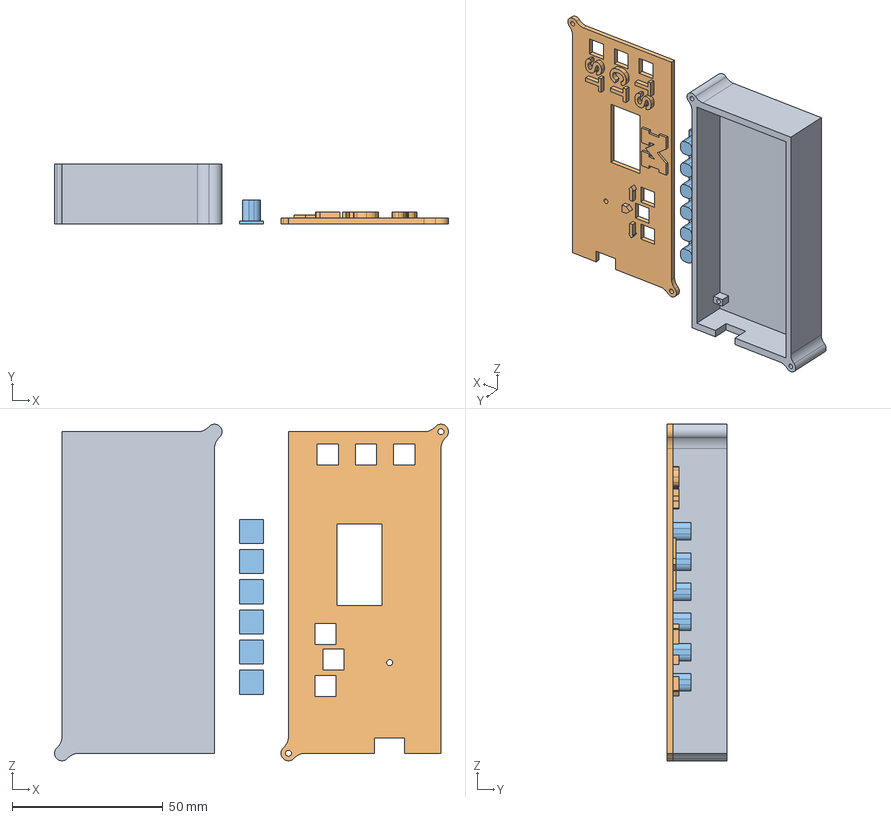
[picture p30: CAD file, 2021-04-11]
CAD/Remote/AE405 Remote Case v4.step
130.5 x 20.0 x 111.5 mm

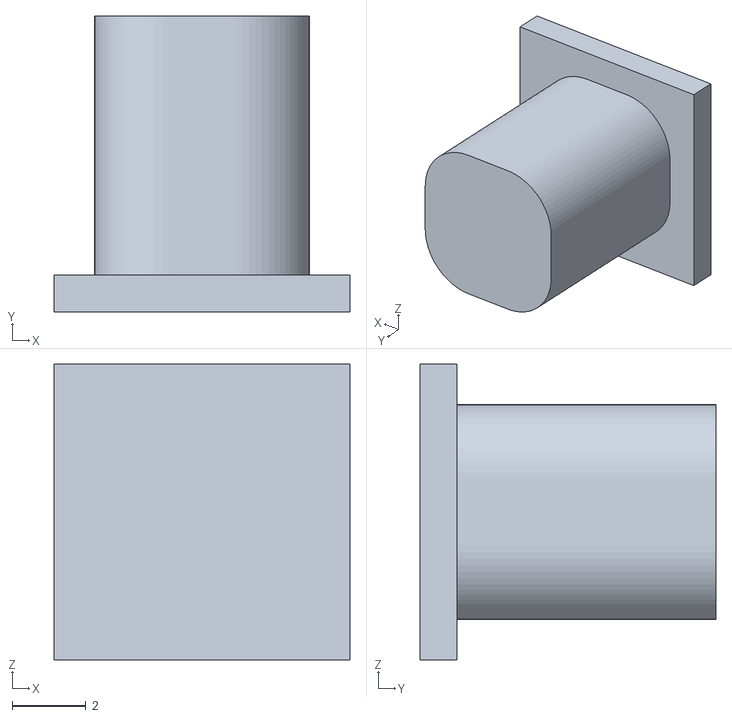
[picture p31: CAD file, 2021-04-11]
CAD/Remote/Buttonx6.stl
8.00 x 8.00 x 8.00

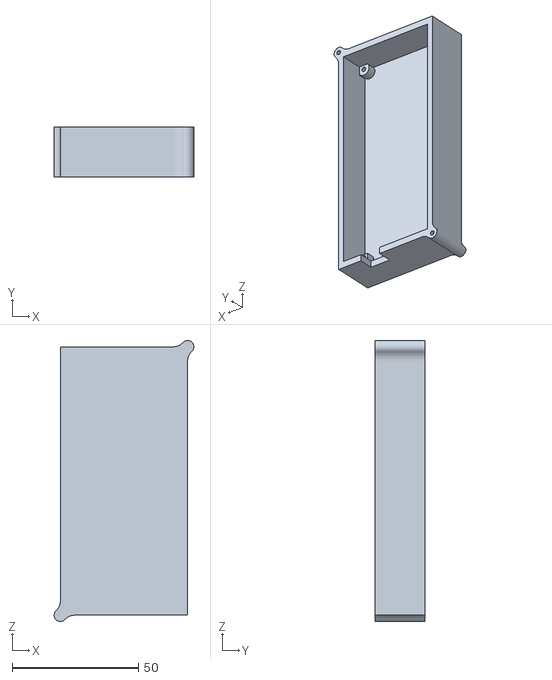
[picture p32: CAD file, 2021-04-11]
CAD/Remote/Base.stl
55.5 x 20.0 x 111.5

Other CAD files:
CAD/Remote/AE405 Remote Case v4.f3d

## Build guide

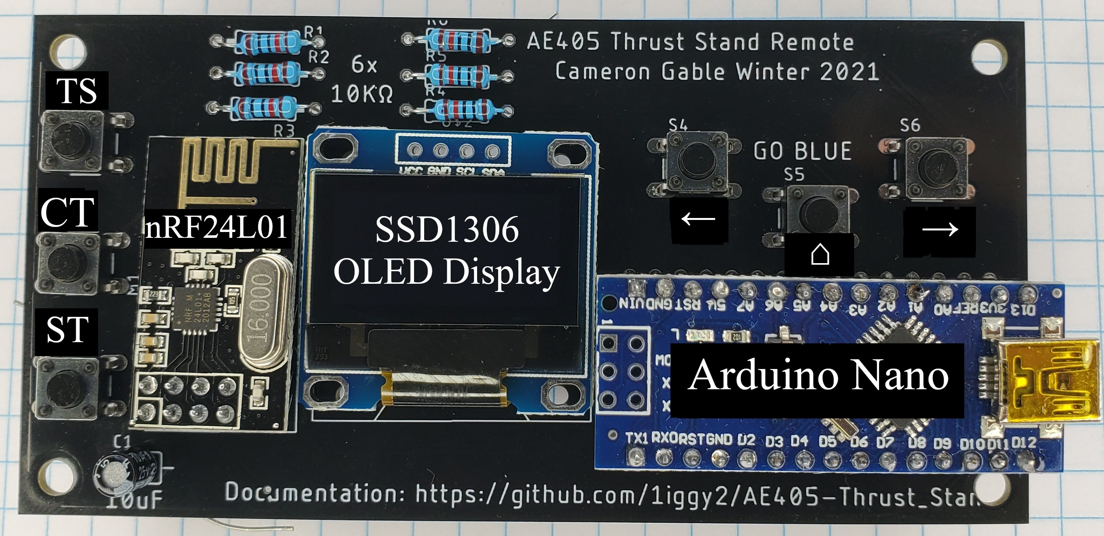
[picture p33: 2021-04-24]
Images/RemoteAssembledPCB_annotated.jpg

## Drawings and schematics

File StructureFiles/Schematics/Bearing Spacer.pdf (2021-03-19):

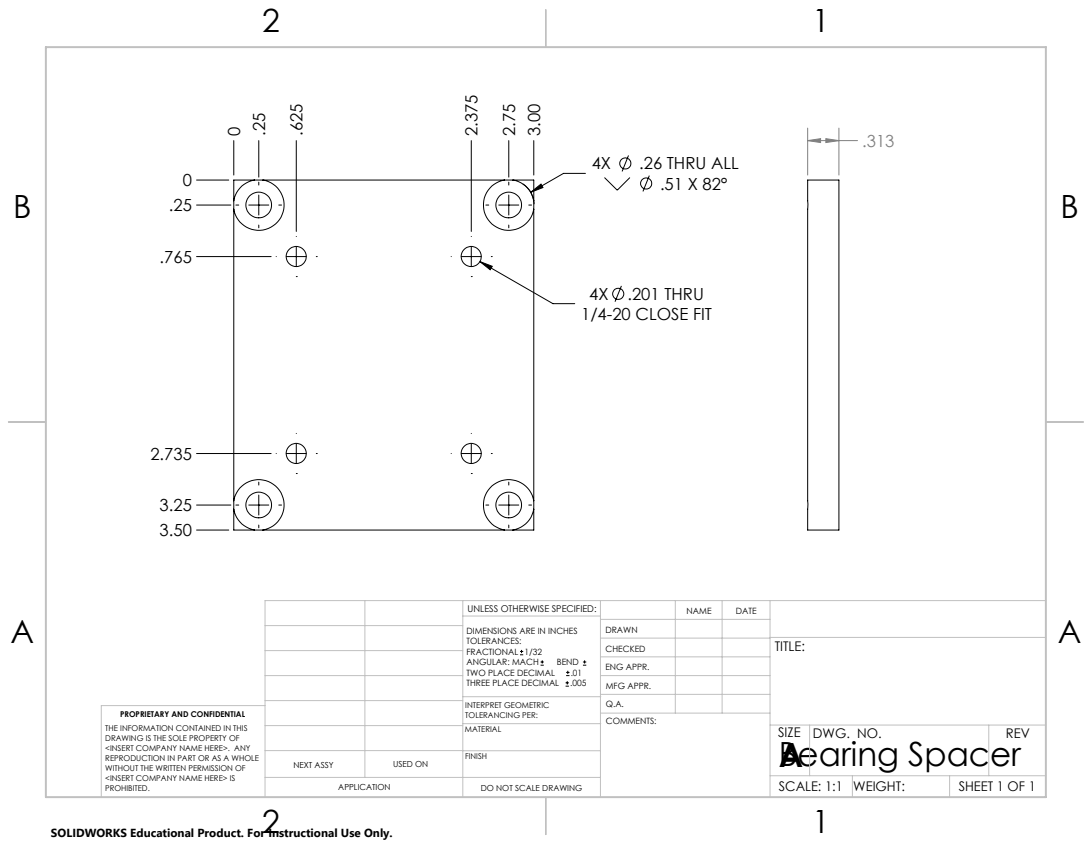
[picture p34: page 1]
.26 THRU ALL; 4X .201 THRU 1/4-20 CLOSE FIT

UNLESS OTHERWISE SPECIFIED: | | NAME | DATE
DIMENSIONS ARE IN INCHES TOLERANCES: FRACTIONAL 1/32 ANGULAR: MACH BEND TWO PLACE DECIMAL .01 THREE PLACE DECIMAL .005 | DRAWN

CHECKED | | | TITLE:

ENG APPR.
MFG APPR.

INTERPRET GEOMETRIC TOLERANCING PER: | Q.A.
MATERIAL | | SIZE Bearing Spacer A | DWG. NO. | REV

PROPRIETARY AND CONFIDENTIAL
THE INFORMATION CONTAINED IN THIS
DRAWING IS THE SOLE PROPERTY OF
<INSERT COMPANY NAME HERE>. ANY
REPRODUCTION IN PART OR AS A WHOLE
WITHOUT THE WRITTEN PERMISSION OF
<INSERT COMPANY NAME HERE> IS
PROHIBITED.

NEXT ASSY | USED ON | FINISH

APPLICATION | DO NOT SCALE DRAWING | | SCALE: 1:1 | WEIGHT: | SHEET 1 OF 1

SOLIDWORKS Educational Product. For Instructional Use Only.

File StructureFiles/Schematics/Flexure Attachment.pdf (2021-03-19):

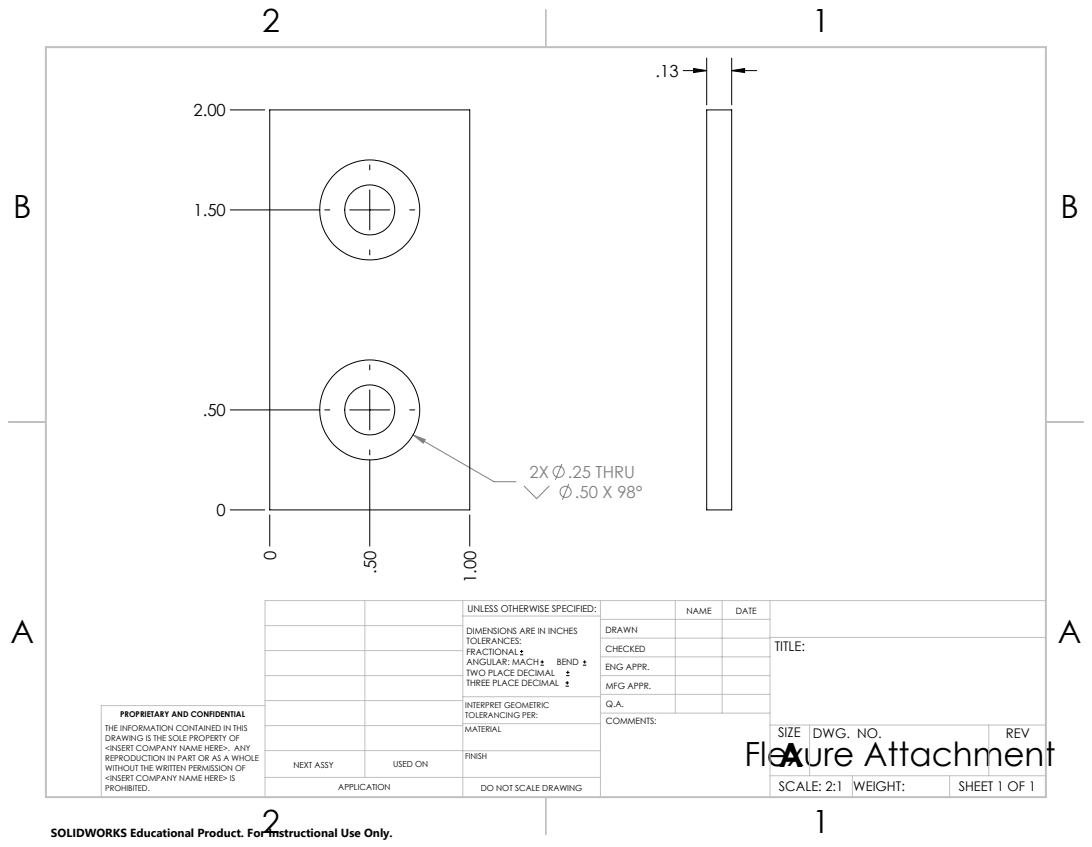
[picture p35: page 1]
2X .25 THRU .50 X 98°; Flexure Attachment

UNLESS OTHERWISE SPECIFIED: | | NAME | DATE
DIMENSIONS ARE IN INCHES TOLERANCES: FRACTIONAL ANGULAR: MACH BEND TWO PLACE DECIMAL THREE PLACE DECIMAL | DRAWN

CHECKED | | | TITLE:

ENG APPR.
MFG APPR.

INTERPRET GEOMETRIC TOLERANCING PER: | Q.A.
MATERIAL | | SIZE A | DWG. NO. | REV

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

NEXT ASSY | USED ON | FINISH

APPLICATION | DO NOT SCALE DRAWING | | SCALE: 2:1 | WEIGHT: | SHEET 1 OF 1

SOLIDWORKS Educational Product. For Instructional Use Only.

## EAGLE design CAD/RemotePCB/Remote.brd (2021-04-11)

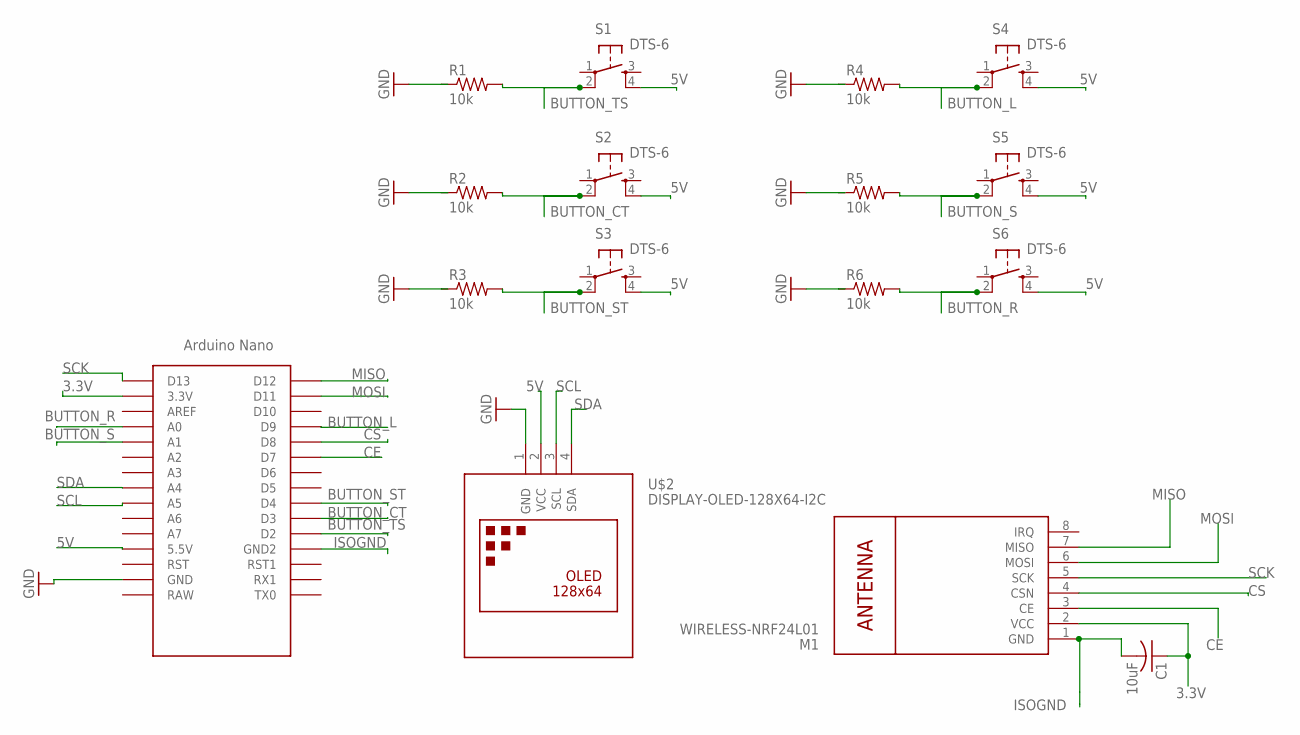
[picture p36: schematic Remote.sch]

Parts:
C1: 10uF; C025-030X050
M1: WIRELESS-NRF24L01
R1, R2, R3, R4, R5, R6: 10k; 0207/10
S1, S2, S3, S4, S5, S6: DTS-6
U$1: NANO
U$2: DISPLAY-OLED-128X64-I2C

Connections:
3.3V: C1.1, M1.2 (VCC), U$1.3.3V
5V: S1.4, S2.4, S3.4, S4.4, S5.4, S6.4, U$1.5V (5.5V), U$2.2 (VCC)
BUTTON_CT: R2.2, S2.2, U$1.D3
BUTTON_L: R4.2, S4.2, U$1.D9
BUTTON_R: R6.2, S6.2, U$1.A0
BUTTON_S: R5.2, S5.2, U$1.A1
BUTTON_ST: R3.2, S3.2, U$1.D4
BUTTON_TS: R1.2, S1.2, U$1.D2
CE: M1.3 (CE), U$1.D7
CS: M1.4 (CSN), U$1.D8
GND: R1.1, R2.1, R3.1, R4.1, R5.1, R6.1, U$1.GND, U$2.1 (GND)
ISOGND: C1.2, M1.1 (GND), U$1.GND1 (GND2)
MISO: M1.7 (MISO), U$1.D12
MOSI: M1.6 (MOSI), U$1.D11
SCK: M1.5 (SCK), U$1.D13
SCL: U$1.A5, U$2.3 (SCL)
SDA: U$1.A4, U$2.4 (SDA)

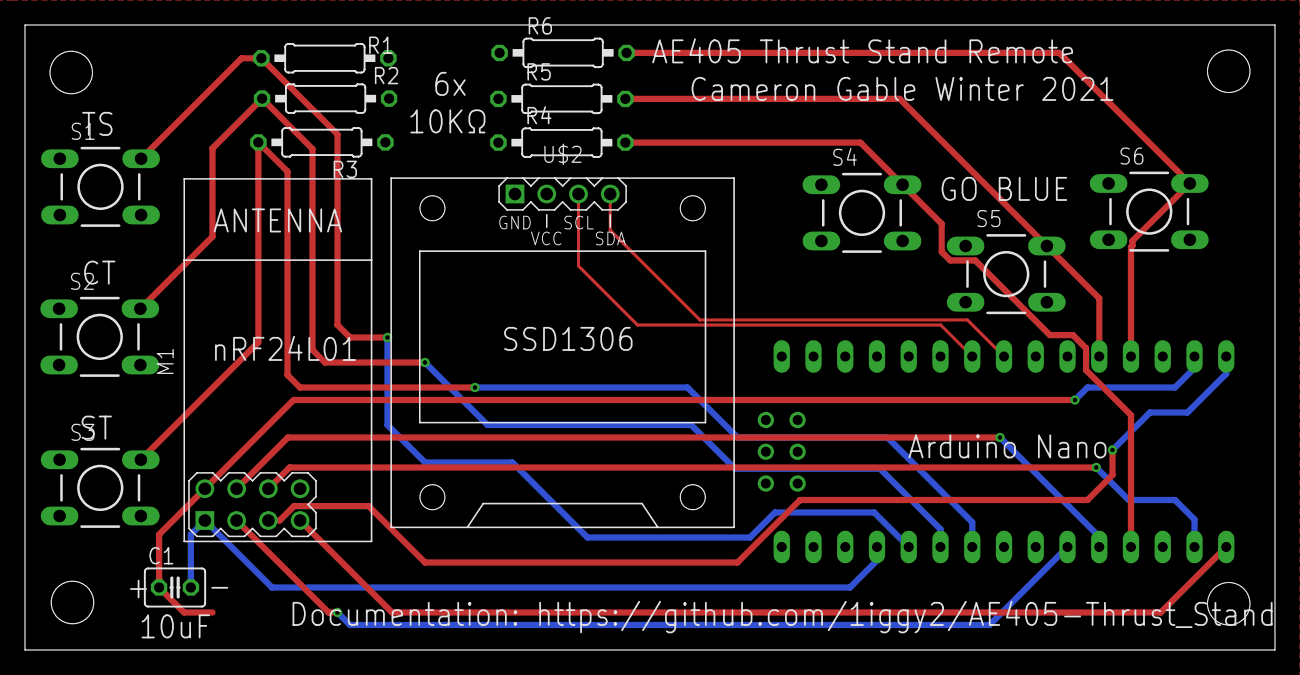
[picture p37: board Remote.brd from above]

Board: 2 copper layers, 100.0 x 50.0 mm, 16 parts (0 on the bottom side), 17 nets.

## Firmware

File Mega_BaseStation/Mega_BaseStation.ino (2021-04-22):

//AERO 405 Thrust Test Stand Code-Base Station
// Cameron Gable | 3/15/2021

//------------------------------------------Libraries
//nRF24L01
  #include <SPI.h>
  #include <nRF24L01.h>
  #include <RF24.h>
  
//BME280
  #include <Adafruit_BME280.h>

//ESC Use
  #include <Servo.h>

//Time based commands
  #include <Time.h>
  #include <TimeLib.h>

//SD Card
  #include <SD.h>

//------------------------------------------Global Set Up
//nRF24L01: https://lastminuteengineers.com/nrf24l01-arduino-wireless-communication/
  #define CE_PIN   7
  #define CSN_PIN 8

  const byte thisSlaveAddress[5] = {'R','x','A','A','A'};
  RF24 radio(CE_PIN, CSN_PIN);

  char MenuNumber[17];
  bool newData = false;
  
  char charA[2] = {'0','\0'};
  char charBBB[4] = {'0','0','0','\0'};
  char charCCC[4] = {'0','0','0','\0'};
  char charDDD[4] = {'0','0','0','\0'};
  char charEEE[4] = {'0','0','0','\0'};
  int A = 0;
  int BBB = 0;
  int CCC = 0;
  int DDD = 0;
  int EEE = 0;
  const char Seperator = ':';

//------------------------------------------Sensor Pin Declaration
//If confused reference this pinout diagram:
    // https://www.javatpoint.com/arduino-mega-pinout
  #define LCPin A0      //Wire LC Voltage (O+) wire to pin A0
  //See Datasheet page 12 for wiring information:
    // http://www.farnell.com/datasheets/2864809.pdf
  //NOTE:   V+ goes to 5V
        //  0+ pin to A0
        //  COM to Ground
  #define IoutPin A1    //Wire KR-Sense Iout to pin A1
  #define VoutPin A2    //Wire KR-Sense Vout to pin A2
  //NOTE:   Connect "⏚" Pin to Ground    

  //Hall Effect Sensor
    //SS49E DataSheet: https://www.addicore.com/SS49E-Linear-Hall-Sensor-p/ad316.htm
    //Pin 1 -> 5V
    //Pin 2 -> Ground
    //Pin 3 -> A3
  #define HallPin A3

  //Tach
  #define RPMPin 2

  //BME 280
  Adafruit_BME280 bme; //Initialized I2C using default I2C Bus
    //Vin -> 5V
    //SCK -> 21 (SCL)
    //SDI -> 20 (SDA)
    //GND -> GND

  //SD Card Writer
  #define chipSelect 53
    //CS -> 53
    //5V -> 5V
    //GND -> GND
    //CLK -> 52
    //DO -> 50
    //DI -> 51
  
// SD Setup
    File DataOut;
    int TestNumber = 0;
    String TestName = "0_Data.txt";

//ESC Setup
  int ESC_PIN = 6;
  Servo esc;

//------------------------------------------Variable Set Up
//Buttons
  const int SensorOutButtonPin = 9;   //"Button 1"
  const int CalibrationButtonPin = 10; //"Button 2"
  const int SettingButtonPin = 11;     //"Button 3"
  int SensorOutButtonState = 0;
  int CalibrationButtonState = 0;
  int SettingButtonState = 0;
  
//Testing Global Variables
  float Throttle_Start = 0;
  float Throttle_End = 0;
  int Throttle_Step = 0;
  float Step_Time = 0;
  float Throttle_High = 0;
  float Throttle_Low = 0;
  float Test_Time = 0;
  unsigned long TestStartTime;
  unsigned long CurrentTestTime;
  unsigned long currentMillis; //Timing Vars
  unsigned long currentMillis2;
  unsigned long prevMillis;
  unsigned long prevMillis2;  
  bool Disp_Thrust = false;
  bool Disp_Torque = false;
  bool Disp_RPM = false;
  bool Disp_VoltAmp = false;
  bool Thrust_Cal = false;
  bool Torque_Cal = false;
  bool ESC_Cal = false;
  bool VoltAmp_Cal = false;

  //RPM Test Variables
  int RPMread1 = 0;
  int RPMread2 = 0;
  unsigned long RPMfirst;
  unsigned long RPMsecond;

//Data Storage Variables
  float LCval = 0;
  float Voltval = 0;
  float Currval = 0;
  float Hallval = 0;
  unsigned long RPMval = 0;

  //BME 280
  float BMEtempFloat = 0;
  float BMEpressFloat = 0;

  //Calibrated Values
  float Force_on_LC = 0; //Value LC sees without moment arm considerations
  float LCval_cal = 0;
  float Voltval_cal = 0;
  float Currval_cal = 0;
  float Hallval_cal = 0;
  float RPMval_cal = 0;

  //Human Readable Power Values
  float Voltage = 0;
  float Amp = 0;
  float Power = 0;

  //Calibration Factors
  float LCcal_factor = .0166;      //From the datasheet by the 4V range and 50lb capacity
  int LC_tare = 0;
  float Voltcal_factor = 0.0773;  //Takes Vout and converts to source voltage /13 from testing R^2=1
  //float Currcal_factor = 1.535/7.5;   //Takes Iout and converts to source current
  float Currcal_factor = 0.17238;
  float Hallcal_factor = 1;       //UNKNOWN AND Based off flexure
  float RPMcal_factor = 60000;    //MS per Minute

  //Default Settings
  float Warn_Volt = 3.4;
  float Min_Volt = 2.8;
  float Max_Amp = 75;
  float Max_Power = 1500;
  int Config_Num = 1;

  int Throttle = 1000;

  
void setup() {
  Serial.begin(9600);
  while (!Serial) {
    Serial.begin(9600);
  }
  //nRF24L01 Setup
  Serial.println("Radio Comms Starting");
  radio.begin();
  radio.setDataRate( RF24_250KBPS );
  radio.openReadingPipe(1, thisSlaveAddress);
  radio.startListening();
    
  //Sensor Pin Initialization
  pinMode(LCPin, INPUT);
  pinMode(IoutPin, INPUT);
  pinMode(VoutPin, INPUT);
  pinMode(HallPin, INPUT);  
  pinMode(RPMPin, INPUT);


  //ESC Setup -- THIS BREAKS EVERYTHING
  esc.attach(ESC_PIN);
  esc.writeMicroseconds(1000);

  //BME280 Setup
  unsigned status;
  status = bme.begin();
  if (!status) {
    Serial.println("Could not find a valid BME280 sensor, check wiring, address, sensor ID!");
    Serial.print("SensorID was: 0x"); Serial.println(bme.sensorID(),16);
    Serial.print("        ID of 0xFF probably means a bad address, a BMP 180 or BMP 085\n");
    Serial.print("   ID of 0x56-0x58 represents a BMP 280,\n");
    Serial.print("        ID of 0x60 represents a BME 280.\n");
    Serial.print("        ID of 0x61 represents a BME 680.\n");
  }

  //Initial Data Gathering
  AmbientMeasure();

  //SD Setup
  pinMode(chipSelect,OUTPUT);
  if (!SD.begin(chipSelect)) {
    Serial.println("initialization failed!");
    //while (1);
  }

  while(SD.exists(TestName)){
    TestNumber = TestNumber + 1; //Iterate number checked for
    TestName = TestNumber + "_Data.txt";
  }

  DataOut = SD.open(TestName, FILE_WRITE);
  if (DataOut){
    Serial.print("Writing SD Header...");
    DataOut.println("AE405 Thrust Stand,,Winter 2021,,");
    DataOut.println("Cameron Gable, Hogan Hsu, Anthony Russo");
    DataOut.println("Brian Sandor, Sergio Ramirez Sabogal");
    DataOut.println("");
    DataOut.println("Find Documentation at:,,https://github.com/1iggy2/AE405-Thrust_Stand");
    DataOut.println("");
    DataOut.println("Ambient Conditions:");
    DataOut.print("Temperature:,");
    DataOut.print(BMEtempFloat);
    DataOut.println(", Celsius");
    DataOut.print("Pressure:,");
    DataOut.print(BMEpressFloat);
    DataOut.println(", Pascals");
    DataOut.println("");
    DataOut.println("Throttle,Time (ms),Thrust (N),Volts,Amps,Torque (in-lb)");
    DataOut.close();
    Serial.println("done.");
  }else{
    Serial.println("Error opening data file");
  }
    
  
  
}

void loop() {
  if (A == 0){              //Gather Remote Data
    RemoteCommunication();
    CheckButtonStatus();
  }else if(A == 1){         //Throttle Sweep
    Throttle_Start = (float)1000+10*BBB;
    Throttle_End = (float)1000+10*CCC;
    Test_Time = (float)DDD*1000; //Seconds to MS
    Step_Time = (float)EEE*1000; //Seconds to MS
    ThrottleSweep();    //Run Subfunction
    
  }else if(A == 2){         //Constant Throttle
    Throttle_Start = (float)1000+10*BBB;
    Test_Time = (float)DDD*1000; //Seconds to MS
    ConstantThrottle(); //Run Subfunction
    
  }else if(A == 3){         //Stress Test
    Throttle_High = (float)1000+10*BBB;
    Throttle_Low = (float)1000+10*CCC;
    Test_Time = (float)DDD*1000;
    Step_Time = (float)EEE*1000;
    StressTest();       //Run Subfunction
    
  }else if(A == 4){         //Sensor Output     BEGIN SERIAL OPERATIONS
    GetSensorOutputParameters();
    SensorOutput();     //Run Subfunction
    
  }else if(A == 5){         //Calibration
    GetCalibrationParameters();
    Calibration();      //Run Subfunction
    
  }else if(A == 6){         //Edit Settings
    GetSettingsParameters(); //Gather Settings
  }else{
    A = 0; //If outside bounds gather remote signal again.
  }
  

}


//------------------------------------------Main Helper Functions
void RemoteCommunication(){
  //Serial.println("Trying to read data ");
  if ( radio.available() ) {
        radio.read( &MenuNumber, sizeof(MenuNumber) );
        newData = true;
    } else {
      //Serial.println("Read Failure");
    }
  if (newData == true) {
      //Serial.print("Data received ");
      //Serial.println(MenuNumber);
      GroupRemoteMessage();      
      newData = false;
  }
}


void GroupRemoteMessage(){
  charA[0] = MenuNumber[0];
  charBBB[0] = MenuNumber[2];
  charBBB[1] = MenuNumber[3];
  charBBB[2] = MenuNumber[4];
  charCCC[0] = MenuNumber[6];
  charCCC[1] = MenuNumber[7];
  charCCC[2] = MenuNumber[8];
  charDDD[0] = MenuNumber[10];
  charDDD[1] = MenuNumber[11];
  charDDD[2] = MenuNumber[12];
  charEEE[0] = MenuNumber[14];
  charEEE[1] = MenuNumber[15];
  charEEE[2] = MenuNumber[16];
  //Serial.print("Saved ID = ");
  //Serial.print(charA);
  //Serial.print(" ");
  //Serial.print(charBBB);
  //Serial.print(" ");
  //Serial.print(charCCC);
  //Serial.print(" ");
  //Serial.print(charDDD);
  //Serial.print(" ");
  //Serial.println(charEEE);
  A = atoi(charA);
  BBB = atoi(charBBB);
  CCC = atoi(charCCC);
  DDD = atoi(charDDD);
  EEE = atoi(charEEE);
  //Serial.print("Saved Ints = ");
  //Serial.print(A);
  //Serial.print(" ");
  //Serial.print(BBB);
  //Serial.print(" ");
  //Serial.print(CCC);
  //Serial.print(" ");
  //Serial.print(DDD);
  //Serial.print(" ");
  //Serial.println(EEE);
}

void AmbientMeasure(){
  Measure280();
}

void Measure280(){
  BMEtempFloat = bme.readTemperature();
  BMEpressFloat = bme.readPressure();
}

void PostTestReset(){
  Serial.println();
  Serial.println("Test Complete");
  esc.writeMicroseconds(1000);
  MenuNumber[17];
  A = 0;
  while(true){
    //Serial.println("Testing Complete");
    }
}

void CheckButtonStatus(){
  SensorOutButtonState = 0;   //Reset Button States
  CalibrationButtonState = 0;
  SettingButtonState = 0;
  SensorOutButtonState = digitalRead(SensorOutButtonPin);   //Read Button States
  CalibrationButtonState = digitalRead(CalibrationButtonPin);
  SettingButtonState = digitalRead(SettingButtonPin);
  ButtonInterpretation(); //Interpret the press
}

void ButtonInterpretation(){
  if(SensorOutButtonState){
    A = 4;
  }else if(CalibrationButtonState){
    A = 5;
  }else if(SettingButtonState){
    A = 6;
  }
}

void ThrottleSweep(){
  TestStartTime = millis();
  float FloatTS = (Throttle_End-Throttle_Start)/(Test_Time/Step_Time);
  Throttle_Step = (int) FloatTS;
  Serial.print("Throttle Step Size: ");
  Serial.println(Throttle_Step);
  Throttle = Throttle_Start;
  LC_tare = analogRead(LCPin);
  while(Throttle < Throttle_End){
    //Serial.println("Throttle Sweep Main");
    //Serial.print("Throttle Setting: ");
    //Serial.print(Throttle);
    esc.writeMicroseconds(Throttle);
    currentMillis = millis();
    //Serial.print("Current Millis: ");
    //Serial.println(currentMillis);
    prevMillis = millis();
    while(prevMillis - currentMillis <= Step_Time){
      //Serial.println("Throttle Sweep Subloop");
      Measure();
      prevMillis = millis();
      //Serial.print("Prev Millis: ");
      //Serial.println(prevMillis);
    }
    //Serial.println("STEP");
    Throttle = Throttle + Throttle_Step;
  }
  PostTestReset();
}

void ConstantThrottle(){
  Serial.println("In Constant Throttle");
  esc.writeMicroseconds(Throttle_Start);
  Serial.print("Testing Throttle: ");
  Serial.println(Throttle_Start);
  currentMillis = millis();
  prevMillis = millis();
  LC_tare = analogRead(LCPin);
  while(prevMillis - currentMillis <= Test_Time){
    Measure();
    prevMillis = millis();
  }
  PostTestReset();
}
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

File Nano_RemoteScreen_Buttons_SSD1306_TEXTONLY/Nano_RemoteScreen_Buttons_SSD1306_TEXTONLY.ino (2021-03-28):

//AERO 405 Thrust Test Stand Code-Remote Screen
// Cameron Gable 3/16/2021

//------------------------------------------Libraries
// SSD1306 Text Only
  #include <SPI.h>
  #include <SSD1306_text_I2C.h>
  #include <ssdfont.h>
  #include <stdlib.h>


//nRF24L01
  //#include <SPI.h> //Shared Dependancy
  #include <nRF24L01.h>
  #include <RF24.h>

//------------------------------------------Global Set Up
//Screen Text Only
  // Hardware SPI pins include D11=Data and D13=Clk
  SSD1306_text oled;
  
//nRF24L01: https://lastminuteengineers.com/nrf24l01-arduino-wireless-communication/
  #define CE_PIN   7
  #define CSN_PIN 8
  
  const byte slaveAddress[5] = {'R','x','A','A','A'};
  RF24 radio(CE_PIN, CSN_PIN); // Create a Radio

  char MenuNumber[17];
  char A;
  char BBB[3];
  char CCC[3];
  char DDD[3];
  char EEE[3];
  
//Buttons
  const int ThrottleSweepButtonPin = 2;     //"Button 1" -> D2
  const int ConstantThrottleButtonPin = 3;  //"Button 2" -> D3
  const int StressTestButtonPin = 4;        //"Button 3" -> D4
  const int LeftButtonPin = 9;              //"Button 4" -> D9
  const int RightButtonPin = A0;            //"Button 5" -> A0
  const int SelectionButtonPin = A1;        //"Button 6" -> A1

  int ConstantThrottleButtonState = 0;
  int ThrottleSweepButtonState = 0;
  int StressTestButtonState = 0;
  int LeftButtonState = 0;
  int RightButtonState = 0;
  int SelectionButtonState;

//General
  int PageSelector = 0;
  bool Confirmed = false;

  char Value1 = '0'; //Number Selection Values
  char Value2 = '0';
  char Value3 = '0';

  char buf[3] = {'0','0','0'};
  const char SelectRange[] = {'0','1','2','3','4','5','6','7','8','9'};

  unsigned long currentMillis;
  unsigned long prevMillis;
  unsigned long txIntervalMillis = 1000;

  int SelectIterator = 0;

  bool Press1 = false;
  bool Press2 = false;
  bool Press3 = false;
  
void setup() { 
  Serial.begin(9600);
  while (!Serial) {
    Serial.begin(9600);
  }
  Serial.println("Setup Screen");
  //------------------------------------------Screen Set Up
    oled.init();
    oled.clear();
    oled.setTextSize(1,1);        // 5x7 characters, pixel spacing = 1
    oled.write("AERO 405 - GO BLUE");
    Serial.println("Waking Up");
    delay(1000);
  //------------------------------------------nRF24L01 Setup
    radio.begin();
    radio.setDataRate( RF24_250KBPS );
    radio.setRetries(3,5); // delay, count
    radio.openWritingPipe(slaveAddress);
    
  //------------------------------------------Button Set Up
    pinMode(ThrottleSweepButtonPin,INPUT);
    pinMode(ConstantThrottleButtonPin,INPUT);
    pinMode(StressTestButtonPin,INPUT);
    pinMode(LeftButtonPin,INPUT);
    pinMode(RightButtonPin,INPUT);
    pinMode(SelectionButtonPin,INPUT);
    
  //------------------------------------------Initialize Splash Screen
    SplashScreen();
    Serial.println("Splashed");
}
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

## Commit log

2021-02-21 Initial Commit, adding previous Arduino Code
2021-03-16 Updated flowcharts to reflect Sensor Output, Calibration, and Settings buttons on Base Station
2021-03-16 Centered flowchart in readme
2021-03-16 Started Base Station Logic Flowchart
2021-03-17 add circuito.io images
2021-03-17 Add circuito remote diagrams to readme
2021-03-18 Updated readme structure, base station wiring guide
2021-03-28 Added Radio and Timing to Base
    Implemented the radio code from BaseStationRadioTest into the main base station function. Tested and working. Implemented millis() based timing to the three test types. Tested and functional. Establi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
2021-03-31 Wrote calibration sketch
    For wiring see comments on the top of the arduino sketch
2021-04-09 Wrote Hall data test into calibration sketch
2021-04-11 Remote Case CAD upload
    [AE405 Remote Case v4.f3d, AE405 Remote Case v4.step, Base.stl, Buttonx6.stl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]
2021-04-11 PCB Designed
    [Remote.brd, Remote.sch, copper_bottom.gbr, copper_top.gbr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]
2021-04-17 Calibration sketch integrated into Base Station Main
    Integrated the tested calibration sketch into the main base station code for testing this weekend. Also uploaded rough EAGLE diagram for base station and removed unnecesarry library. Future Work: Imp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
2021-04-19 Found ESC.attach or ESC.writeMicroseconds breaks everything... Will fix
2021-04-20 Add Case Image
2021-04-21 Debugging Serail Prints
2021-04-21 Debugging Serial Prints V2
2021-04-21 LC, Torque, and Voltage Calibrated
2021-04-21 SD Output Tweaks
    Added time, redid voltage calibration, recentered torque sensor
2021-04-21 Added remote PCB assembled image
2021-04-22 Current Calibration and SD file it change
2021-04-22 Current Calibration update

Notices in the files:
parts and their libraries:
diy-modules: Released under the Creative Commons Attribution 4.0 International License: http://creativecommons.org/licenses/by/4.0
